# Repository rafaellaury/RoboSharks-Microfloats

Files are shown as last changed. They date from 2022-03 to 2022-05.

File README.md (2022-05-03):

# RoboSharks - MicroFloats

Welcome to the Team RoboSharks MicroFloats Github page. I hope you enjoy your stay!

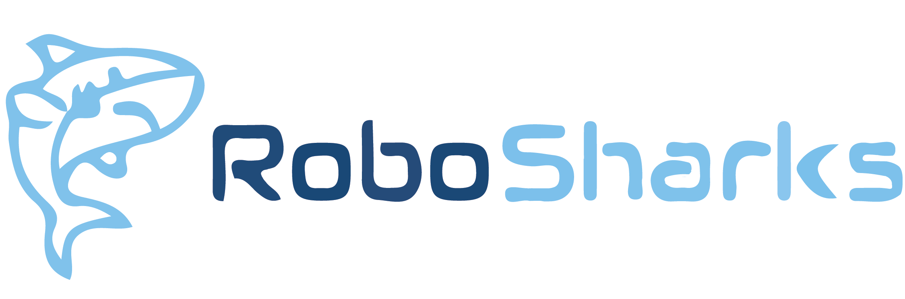
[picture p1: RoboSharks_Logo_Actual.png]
RoboSharks


MicroFloats is a project that aims to develop a swarm of autonomous underwater vehicles for ocean exploration. The current mission it is being developed for is the discovery of larval dispersion. Scientists in Stellwagen Bank, MA are researching this unknown phenomena, and the MicroFloats will greatly aid this scientific discovery effort.

MicroFloats is an ongoing project at Georgia Tech and has had several iterations of Senior Design teams and VIP teams working on it, hence the somewhat disorganized and multilayered structure. The VIP team has a helpful wiki that helps to explain some of the electronics and BMS specifics (link [here](https://github.gatech.edu/mwoodward6/LagrangianProfiler/wiki)!)

Check out our [website](https://eceseniordesign2022spring.ece.gatech.edu/sd22p17/) for more documentation and information about the project! The details of the github are explained below.

## CAD Models

This folder contains all of the CAD models in .SLDPRT format, and were created in SolidWorks. Details on measurements can be found in the fabrication package on our website.

full CAD model

## MatLab Simulations

This folder contains MatLab simulations done for the Power subsystem and antenna range. These give rough metrics for how the MicrFloat will perform since we were not able to test it in full operation.

## PCB

The PCB folder contains three subfolders, one for the Battery Management System (BMS), one for the Sensor Board, and one for the Contorl Board. These all have the most up to date KiCAD PCB schematics and board layouts in there. They also include the latest Gerber and Drill files for assembly, but it is RECOMMENDED to run a DRC again before using these pregenerated files...maybe we missed something!

## Test Code

This folder contains all the code needed to test the MicroFloat and the Sensor board in particular. 

### MicroFloat Test Code

The Arduino test Code for the whole MicroFloat came mostly from the previous team (RUR) and was adapted for our needs. Note: these files are for use with the current electronics prototyping setup, which uses an SAMD51 Thing Plus. You will have to configure your Arduino IDE to interface with this board correctly as described [here.](https://learn.sparkfun.com/tutorials/samd51-thing-plus-hookup-guide/uf2-bootloader--drivers)

The following is the documentation on each of the methods for the MicroFloats test code, taken from RUR's documentation.

The following is a brief overview and description of each test code found in the MicroFloat-Test repository. Most of the code listed is for priming the system and making sure that enough oil is in the bellows versus the reservoir to achieve neutral buoyancy. When using the following programs to calibrate oil levels, it is recommended that the electronics are off to the side so that the cap of the reservoir can be taken off, and the oil levels can be monitored. Watching the oil levels is crucial as contracting or expanding the bellows too much could cause it to pop, and expanding the bellows beyond the amount of oil in the reservoir introduces air to the system. 

*do_nothing*

This program will do as it is called, nothing. This program was written in order to test the float underwater to check neutral buoyancy. It is necessary simply because the power switch at the top of the float needs to be screwed in (and therefore the system is powered). This program ensures that the microcontroller does not send any commands. 

*full_contract*

This program will remove all oil from the bellows and into the reservoir. This would be used if trying to readjust the timings if the oil levels in the reservoir/bellows became inconsistent. This program will run once.

*full_expand*

This program will remove all the oil from the reservoir and into the bellows. This would also be used to readjust the timings if the oil levels in the reservoir/bellows became inconsistent. This program will run once.

*half_contract*

This code will remove half of the oil from the bellows, into the reservoir. This code would be run if the bellows was fully expanded with oil, and the desired state was only half expanded with oil. In this case, the float would then be at neutral buoyancy. This program will run once.

*half_expand*

This code will add half the oil from the reservoir into the bellows. This could be run if the bellows was fully contracted and the desired state was half expanded with oil. In this case, the float would then be at neutral buoyancy. This program will run once. 

*mission*

This is code to be run in a test environment. The code assumes that the starting state is with a  half contract/half expanded bellows (neutral buoyancy). It will then sink the bottom of a pool by half contracting the bellows (resulting in no oil in the bellows). It will then expand half way and wait at the bottom of the pool. The float will then expand the bellows the rest of the way to rise, and then half contract the bellows to reach neutral buoyancy again. This program runs in a loop.

### Sensor Board Test Code

The Sensor Board testing setup is described in the Final Report. Basically, it uses an ARM mbed microcontroller (hence the mbed C++ code) to send RS-232 signals to the Sensor Board, and then reads the I2C output from the Sensor Board using an Arduino. The mbed code needs to be flashed onto the mbed, and then the computer needs to be connected to the Arduino so that the serial monitor can be read to see the I2C addresses and data. The **I2C Demo** code finds the I2C addresses that are currently responding. The other programs can be used to try to get data from the Sensor Board.

## VIP Team Files

This folder contains all the VIP files at the time of our project. This could be used, but it would be better to check on the latest status on the [VIP's actual Github page](https://github.gatech.edu/Aquabots-VIP), where they have links to various useful repositories.

Have fun!

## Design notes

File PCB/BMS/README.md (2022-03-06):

# Battery Management System
For more information please check out our [wiki](https://github.gatech.edu/Aquabots-VIP/BatteryManagementSystem/wiki)!

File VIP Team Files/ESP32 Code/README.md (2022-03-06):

# This folder contains the current code to be run on the microfloat's onboard ESP32-S2

## CaptivePortal
The CaptivePortal code shows a very basic proof of concept to allow the ESP32 to broadcast its own wifi network that automatically redirects you to its webpage when upon connection. This will be necessary when testing without a convinient wifi network for the ESP to connect to but is inconvinient for development since you have to constantly switch wifi networks.

## APServer
The APServer code is where the majority of the funcioning code lives right now. It is much easier to develop code using the APServer version since it connects the ESP32 to a wifi network and allows you to access the gui like a website. Unfortunately it probably won't play nicely with gtwifi so we will need to copy the important parts back to the CaptivePortal version at some point.

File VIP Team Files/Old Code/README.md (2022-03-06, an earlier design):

# This contains the previous code from when the microfloat used a Raspberry Pi for its onboard electronics

It looks like [Lagrangian.py](https://github.gatech.edu/mwoodward6/LagrangianProfiler/blob/master/Old%20Code/Lagrangian.py) is the code designed to run on the Raspberry Pi. There is also [LagrangianSerialLine.py](https://github.gatech.edu/mwoodward6/LagrangianProfiler/blob/master/Old%20Code/LagrangianSerialLine.py) which seems to have been used for manually testing the profiler out of the water (I would recommend focusing more on Lagrangian.py).

[TestControlGui.py](https://github.gatech.edu/mwoodward6/LagrangianProfiler/blob/master/Old%20Code/TestControlGUI.py) seems to be the newest version of the GUI.

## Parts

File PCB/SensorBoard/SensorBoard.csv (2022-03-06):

Id | Designator | Package | Quantity | Designation | Supplier and ref
1 | C8,C7,C6,C5,C4,C3 | C_0603_1608Metric_Pad1.05x0.95mm_HandSolder | 6 | 0.1uF
2 | J1 | PinHeader_2x03_P2.54mm_Vertical | 1 | Power Header
3 | J2 | PinHeader_2x03_P2.54mm_Vertical | 1 | Signal Header
4 | REF**,REF**,REF** | MountingHole_3.2mm_M3_Pad_Via | 3 | MountingHole_3.2mm_M3_Pad_Via
5 | U6,U5,U4,U3 | TSSOP-16_4.4x5mm_P0.65mm | 4 | SC16IS740IPWQ900
6 | U2 | VSSOP-10_3x3mm_P0.5mm | 1 | ADS1115IDGST
7 | U1 | SSOP-28_5.3x10.2mm_P0.65mm | 1 | MCP23017_SS
8 | RLY4,RLY3,RLY2,RLY1,RLY0 | SOP-4_3.8x4.1mm_P2.54mm | 5 | CPC1002NTR
9 | R12,R11,R10,R9,R8,R3,R2,R1,R0 | R_0805_2012Metric_Pad1.15x1.40mm_HandSolder | 9 | 1k
10 | R4 | R_0805_2012Metric_Pad1.15x1.40mm_HandSolder | 1 | 10k
11 | J4 | Molex_Nano-Fit_105314-xx10_2x05_P2.50mm_Horizontal | 1 | Sensor 0
12 | J5 | Molex_Nano-Fit_105314-xx10_2x05_P2.50mm_Horizontal | 1 | Sensor 1
13 | J6 | Molex_Nano-Fit_105314-xx10_2x05_P2.50mm_Horizontal | 1 | Sensor 2
14 | J7 | Molex_Nano-Fit_105314-xx10_2x05_P2.50mm_Horizontal | 1 | Sensor 3
15 | CRYS1 | Crystal_HC49-U_Vertical | 1 | LFXTAL003033BULK
16 | C2 | C_0603_1608Metric_Pad1.05x0.95mm_HandSolder | 1 | 33pf
17 | C1 | C_0603_1608Metric_Pad1.05x0.95mm_HandSolder | 1 | 22pf

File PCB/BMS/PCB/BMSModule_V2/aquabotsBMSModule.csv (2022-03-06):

Id | Designator | Package | Quantity | Designation | Supplier and ref
1 | ATTINY841 | SOIC-14_3.9x8.7mm_P1.27mm | 1 | ATtiny841-SSU
2 | C2 | C_0805_2012Metric | 1 | 1uF
3 | C5,C4 | C_0805_2012Metric | 2 | 22pF
4 | D2 | D_SMB | 1 | SMBJ5.0A
5 | F1 | Fuse_1812_4532Metric | 1 | mSMD150
6 | POWER1 | JST_PH_S2B-PH-K_1x02_P2.00mm_Horizontal | 1 | Battery
7 | Q1 | SOT-23 | 1 | AO3400A
8 | R3 | R_0805_2012Metric | 1 | 6.8K
9 | R4 | R_0805_2012Metric | 1 | 2.7K
10 | R5 | R_0805_2012Metric | 1 | 220OHMS
11 | R8,R12,R25,R26,R29,R30,R24,R6,R22,R32,R39,R33,R31,R36,R38,R35,R34,R37 | R_2010_5025Metric | 18 | 3.3OHM 3/4W
12 | R16 | R_0805_2012Metric | 1 | 4.7KOHMS
13 | R18 | R_0805_2012Metric | 1 | 2.2KOHMS
14 | R19 | R_0805_2012Metric | 1 | CMFB103F3950FANT
15 | R20,R1,R15 | R_0805_2012Metric | 3 | 10KOHMS
16 | RX1 | JST_PH_S2B-PH-K_1x02_P2.00mm_Horizontal | 1 | RX Connector
17 | TX1 | JST_PH_S2B-PH-K_1x02_P2.00mm_Horizontal | 1 | TX Connector
18 | Y1 | Crystal_SMD_5032-2Pin_5.0x3.2mm | 1 | 8MHZ Ceramic Resonator
19 | D4 | LED_0805_2012Metric | 1 | Blue
20 | C1 | C_0805_2012Metric | 1 | 100nF
21 | U1 | SOP-4_4.4x2.6mm_P1.27mm | 1 | EL3H7(B)(TA)-G
22 | R2 | R_0805_2012Metric | 1 | 1KOHMS
23 | D1 | SOT-23 | 1 | AZ432ANTR-E1
24 | R14 | R_0805_2012Metric | 1 | 510OHMS

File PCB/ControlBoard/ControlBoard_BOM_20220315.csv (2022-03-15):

Id | Designator | Package | Quantity | Designation | Supplier and ref
1 | U5 | SOP65P640X110-21N | 1 | TPS75233QPWPR
2 | J8 | USB_C_Receptacle_HRO_TYPE-C-31-M-12 | 1 | USB_C_Receptacle_USB2.0
3 | J3,J4,J5,J6 | Molex_Nano-Fit_105314-xx08_2x04_P2.50mm_Horizontal | 4 | Conn_02x04_Odd_Even
4 | U7 | ublox_NEO | 1 | NEO-M9N
5 | U3 | ESP32-S2-WROOM | 1 | ESP32-S2-WROOM
6 | R29,R36 | R_0603_1608Metric | 2 | 470R
7 | U14,U15 | SOP-4_4.4x2.6mm_P1.27mm | 2 | FODM217C
8 | R31,R38 | R_0603_1608Metric | 2 | 100R
9 | R30,R21,R37 | R_0603_1608Metric | 3 | 100k
10 | Q1,Q3 | SOT-23 | 2 | DMP3030SN-7
11 | D1,D2 | D_0603_1608Metric | 2 | D_Schottky
12 | J2 | PinHeader_2x03_P2.54mm_Vertical | 1 | Power Header
13 | J7 | PinHeader_2x03_P2.54mm_Vertical | 1 | Signal Header
14 | BT1 | BR-1632A_HAN | 1 | BATT_BCKP
15 | C1,C11,C12,C18,C24,C27,C31 | C_0603_1608Metric | 7 | 10uF
16 | C2,C6,C8,C9,C10,C13,C16,C19,C21,C23,C26,C42,C44 | C_0603_1608Metric | 13 | 0.1uF
17 | C3 | C_0603_1608Metric | 1 | 15 uF
18 | C4,C5,C14,C15 | C_0603_1608Metric | 4 | 20pF
19 | C7 | C_0603_1608Metric | 1 | 22uF
20 | C17,C33,C36,C37,C38 | C_1206_3216Metric | 5 | 22uF
21 | C22,C29 | C_0603_1608Metric | 2 | 1.0uF
22 | C34,C35,C39 | C_0603_1608Metric | 3 | 100nF
23 | C40 | C_0805_2012Metric | 1 | 200nF
24 | C41,C43 | CAPC6153X670N | 2 | 22uF
25 | F1,F4 | Fuse_0603_1608Metric | 2 | 2A
26 | F2,F3 | Fuse_0603_1608Metric | 2 | 3A
27 | FB1,FB2 | L_0603_1608Metric | 2 | 1.5A
28 | J1 | U.FL_Hirose_U.FL-R-SMT-1_Vertical | 1 | Conn_Coaxial
29 | J9 | microSD_HC_Wuerth_693072010801 | 1 | Micro_SD_Card
30 | L1 | L_0805_2012Metric | 1 | 2.2 uH
31 | L3 | Vishay-IHLP-3232DZ-FP_2.413x5.334-3D_4.0-0-0-MFG | 1 | 3.3uH
32 | L4 | L_Wuerth_WE-LQS-8040 | 1 | 12uH
33 | Q2 | SOT-23 | 1 | SST3906HZGT116
34 | R1,R8 | R_0603_1608Metric | 2 | 1M
35 | R2 | R_0603_1608Metric | 1 | 732k
36 | R3,R6,R12,R13,R15,R16,R18,R19,R20,R23,R26,R27,R28 | R_0603_1608Metric | 13 | 10k
37 | R4,R5 | R_0603_1608Metric | 2 | 22
38 | R9 | R_0603_1608Metric | 1 | 365k
39 | R14 | R_0603_1608Metric | 1 | 200k
40 | R17 | R_0603_1608Metric | 1 | 54.9k
41 | R22 | R_0603_1608Metric | 1 | 5.23k
42 | R24,R25 | R_0603_1608Metric | 2 | 5.1k
43 | R32,R34 | R_0603_1608Metric | 2 | 1k
44 | R33 | R_0603_1608Metric | 1 | 27k
45 | SW1 | SW_Push_SPST_NO_Alps_SKRK | 1 | Reset
46 | SW2 | SW_Push_SPST_NO_Alps_SKRK | 1 | Boot
47 | SW3 | SW_DIP_SPSTx04_Slide_6.7x11.72mm_W8.61mm_P2.54mm_LowProfile | 1 | SW_DIP_x04
48 | U1 | TSOT-23-5 | 1 | LM3670MF
49 | U2,U6 | MSOP-12-1EP_3x4mm_P0.65mm_EP1.65x2.85mm_ThermalVias | 2 | LTC4419
50 | U4 | InvenSense_QFN-24_3x3mm_P0.4mm | 1 | ICM-20948
51 | U8 | Bosch_LGA-8_2.5x2.5mm_P0.65mm_ClockwisePinNumbering | 1 | BME280
52 | U9 | LR62E | 1 | LR62E
53 | U10 | TSSOP-8_3x3mm_P0.65mm | 1 | PCA9306DP
54 | U11 | SOT-23-6 | 1 | TPS565201
55 | U12 | SOT-23-6 | 1 | TPS54202DDR
56 | U13 | SOT-23-6 | 1 | USBLC6-2SC6
57 | Y1 | Crystal_SMD_3215-2Pin_3.2x1.5mm | 1 | 32.768KHz 12.5p
58 | C25 | C_1206_3216Metric | 1 | 47uF

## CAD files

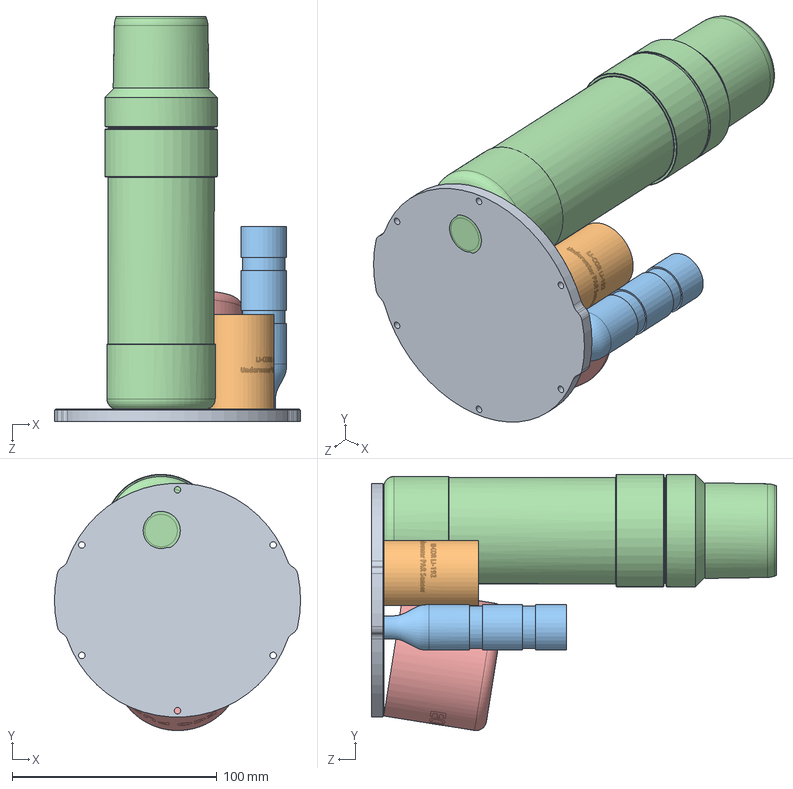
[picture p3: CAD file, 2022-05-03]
CAD Models/Sensors and Top Cap Assembly/Sensor-Top Cap Assembly.SLDASM
120.3 x 125.2 x 198.0 mm
Blue Robotics End Cap
PAR Sensor
Mini CTD
8262-000-28 - Nano SST final assembly with pressure PA-4LD cable connection_Substitute_2.stp
ECO PUCK

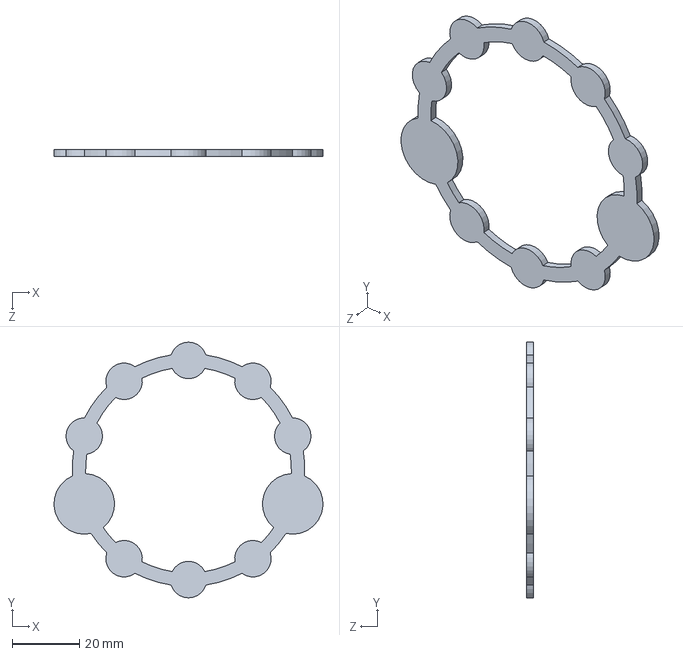
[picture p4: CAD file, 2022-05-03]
CAD Models/BMS_Assembly/Bottom_Bus_Full.SLDPRT
79.8 x 75.9 x 2.03 mm

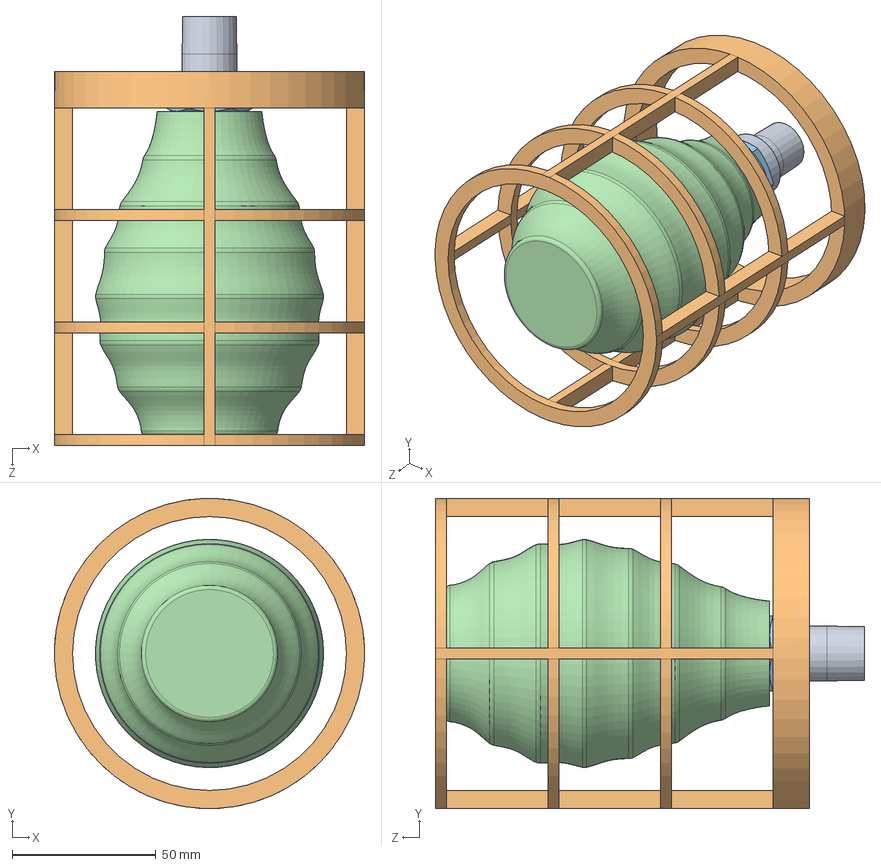
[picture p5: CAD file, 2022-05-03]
CAD Models/Bottom Cap Assembly/RoboSharks Bottom Cap Assembly.SLDASM
108.0 x 108.0 x 149.2 mm
RUR - Pressed Fitting Adaptor
Bellows Cage
4810T364_British Standard Low-Pressure Stainless Steel Pipe Fitting
Bellows

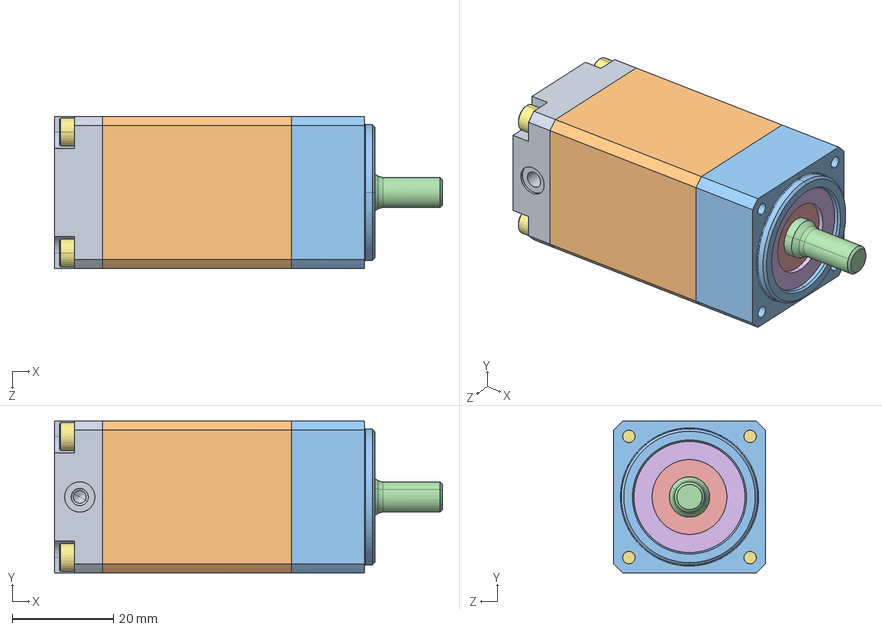
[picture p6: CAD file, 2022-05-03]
CAD Models/Internal Assembly/Takako - Pump - TFH-040.SLDASM
76.8 x 30.0 x 30.0 mm
Part9.IGS
Part10.IGS
Part13.IGS
Part13.1.IGS
Part13.1.2.IGS
Part16.IGS
Part20.IGS x 4

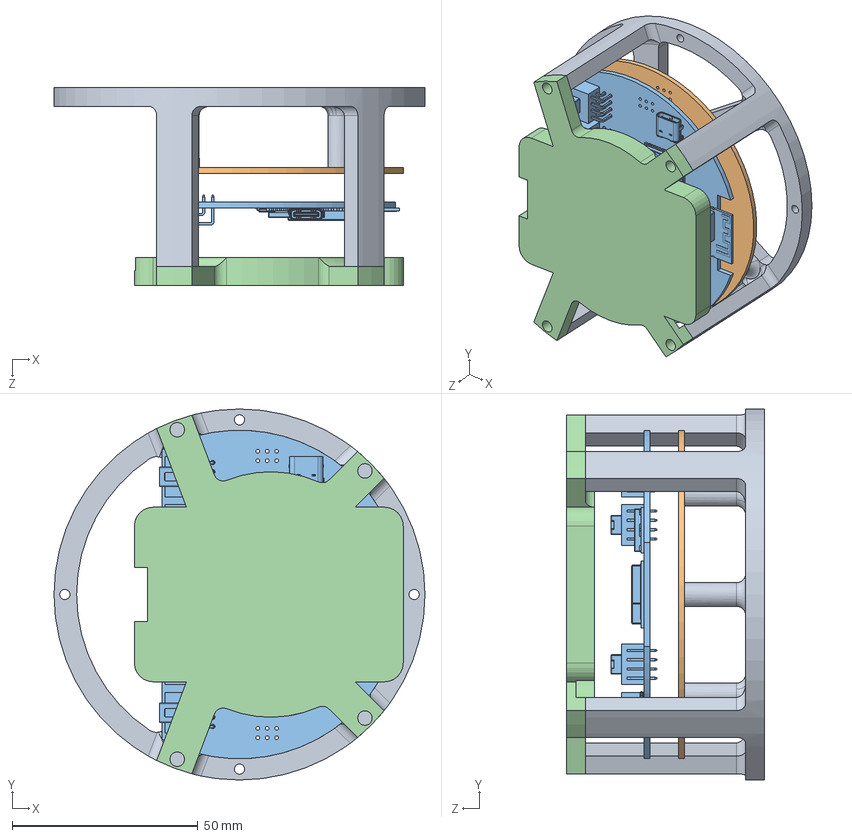
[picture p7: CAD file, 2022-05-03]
CAD Models/PCB files/Electronics Mount Assembly Final.SLDASM
99.8 x 99.8 x 53.3 mm
RoboSharks Electronics Mount
SensorBoard
ControlBoard
Mount Attachment
aquabotsBMSController

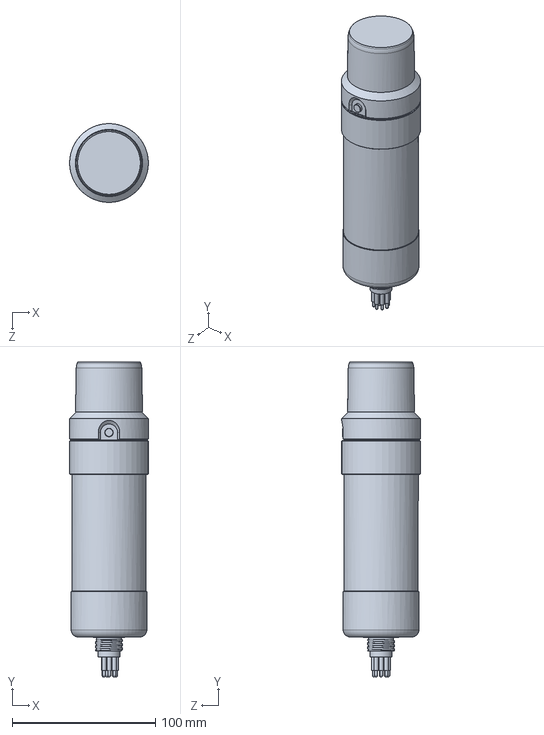
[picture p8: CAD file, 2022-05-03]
CAD Models/Sensors and Top Cap Assembly/Nano with Connector.SLDASM
55.0 x 219.9 x 55.0 mm

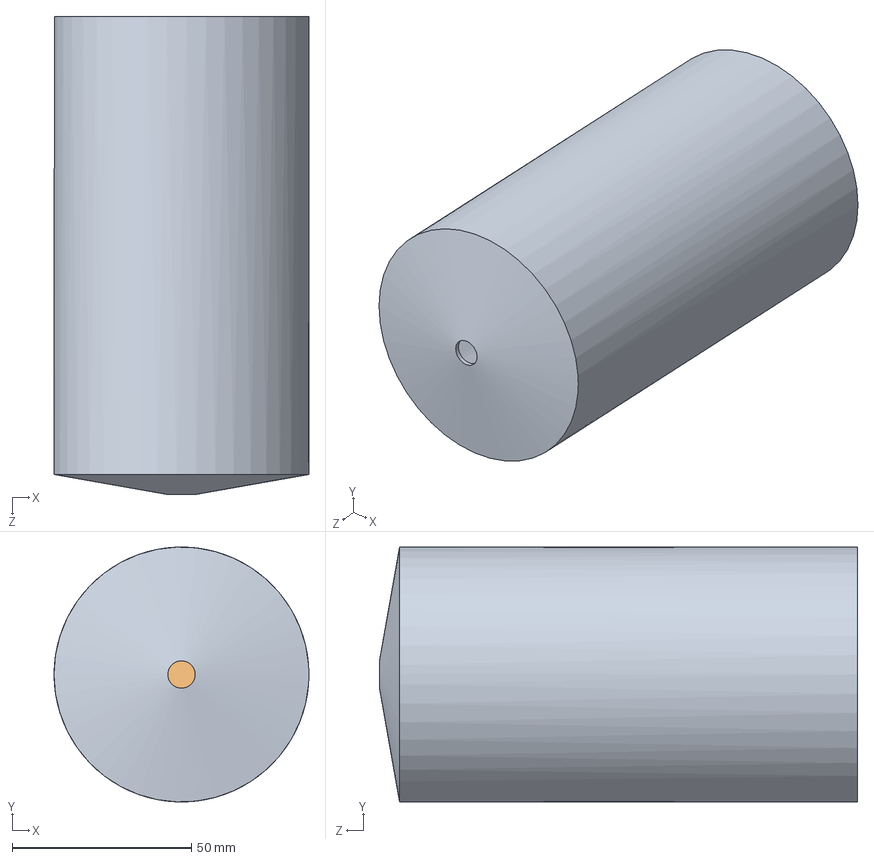
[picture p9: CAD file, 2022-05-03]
CAD Models/Syringe Assembly.SLDASM
71.1 x 71.1 x 133.4 mm
Syringe
Syringe Plunger

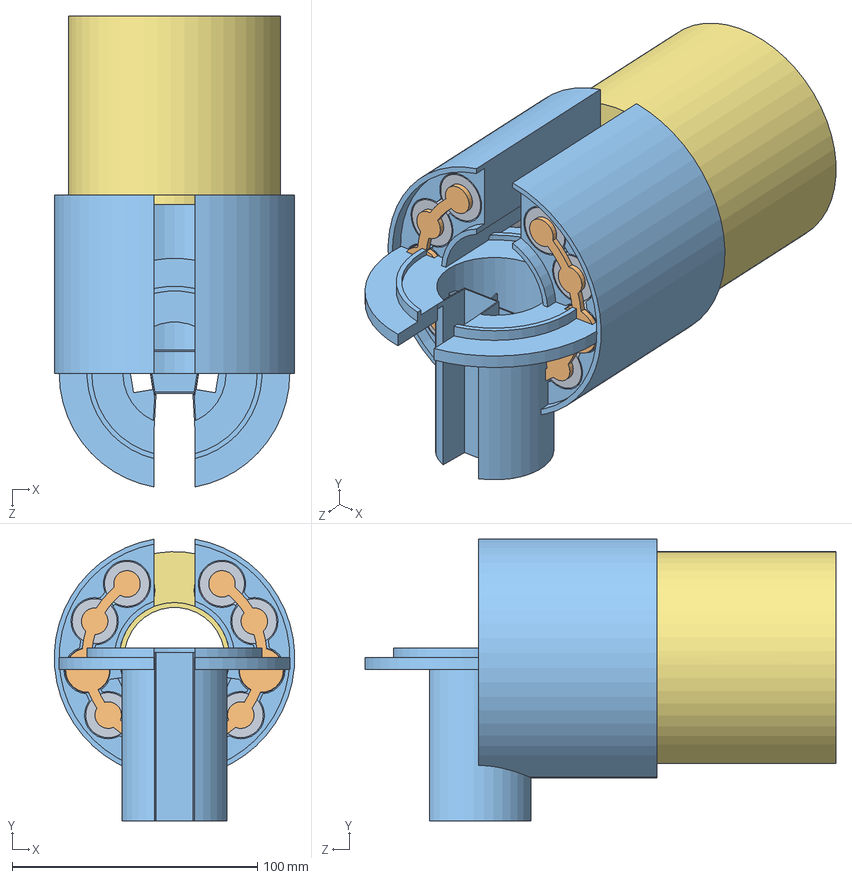
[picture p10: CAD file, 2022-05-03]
CAD Models/BMS_Assembly/BMS_Assembly.SLDASM
97.9 x 114.8 x 191.9 mm
Top_Array
Top_Bus_Half x 2
Top_Case
Bottom_Cap
Bottom_Bus_Full
Bottom_Array
Bottom Case
Bottom_Bus_Half_1
Bottom_Bus_Half_2
Top_Bus_Full
Top_Cap

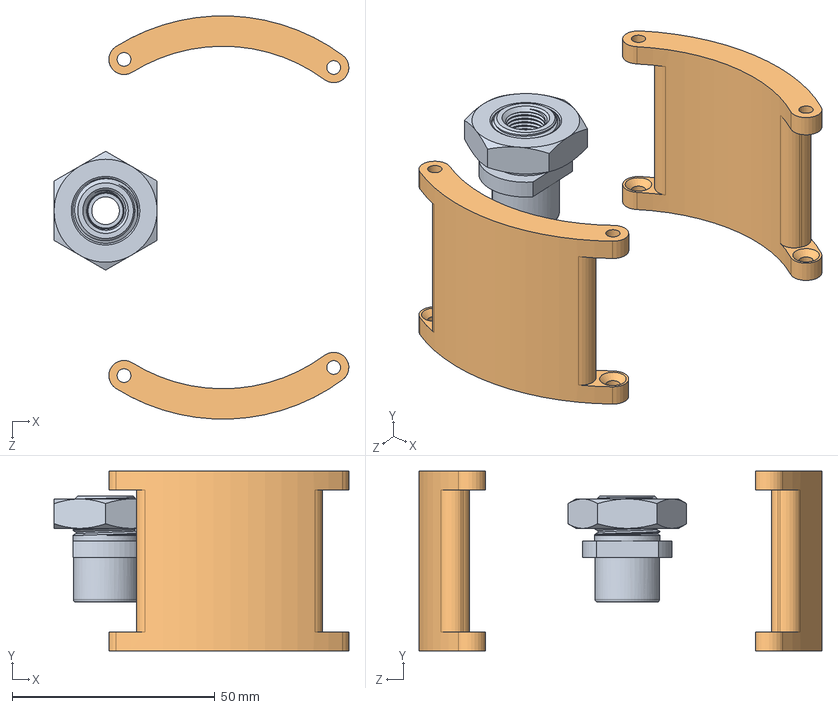
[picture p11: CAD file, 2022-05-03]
CAD Models/Internal Assembly/RUR - Reservoir Assembly.SLDASM
72.7 x 44.3 x 99.4 mm
McMaster - Through Wall Fitting - 8674T54
RUR - Standoff Reservoir x 2

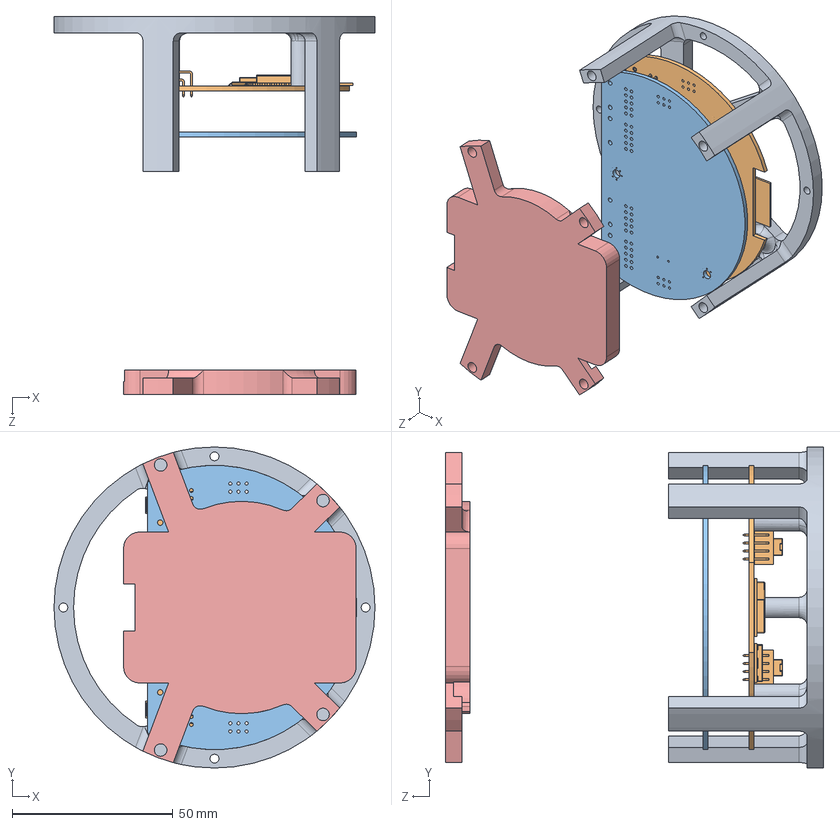
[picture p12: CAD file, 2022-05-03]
CAD Models/PCB files/PCBs and Mount Assembly.SLDASM
99.8 x 99.8 x 117.6 mm
RoboSharks Electronics Mount
ControlBoard
SensorBoard
aquabotsBMSController
Mount Attachment

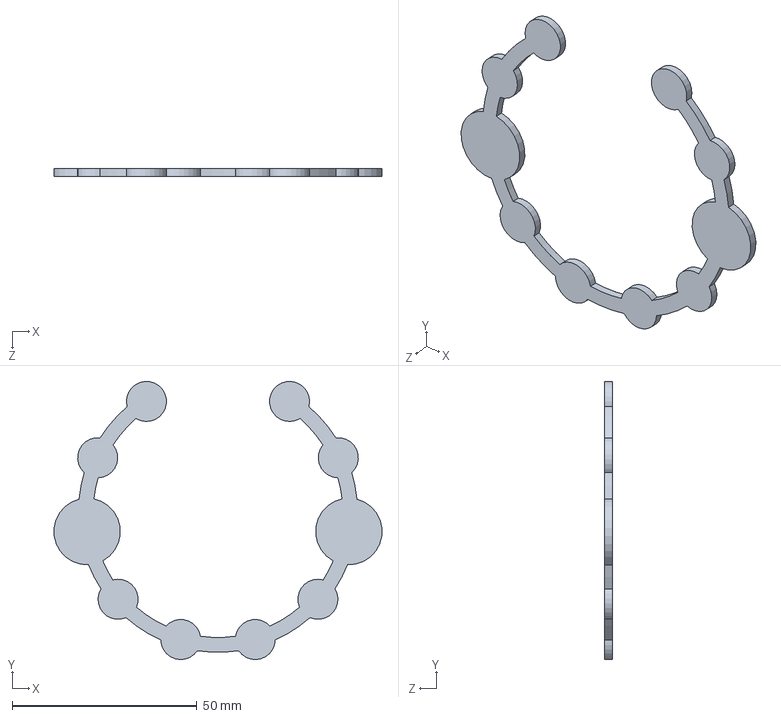
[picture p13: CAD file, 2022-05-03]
CAD Models/BMS_Assembly/Top_Bus_Full.SLDPRT
88.7 x 75.2 x 2.03 mm

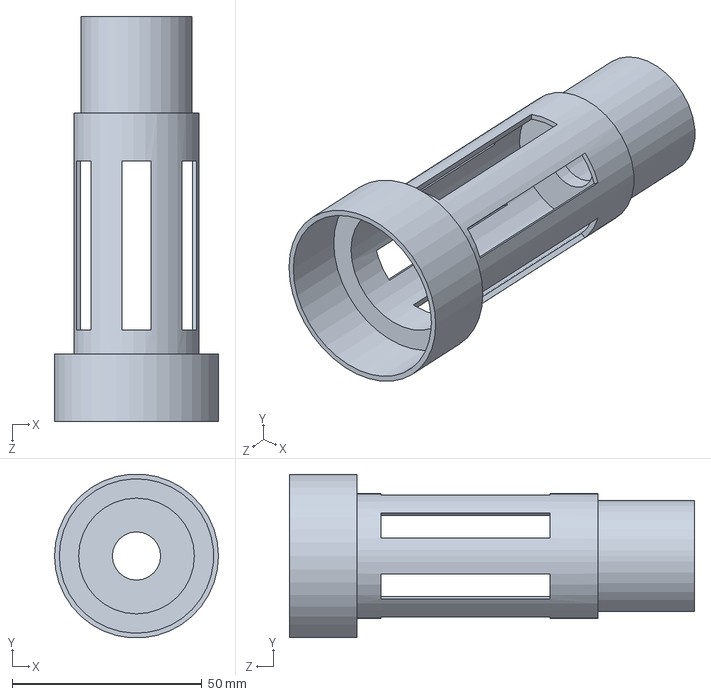
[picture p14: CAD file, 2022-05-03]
CAD Models/Antenna/Antenna Mount.SLDPRT
43.2 x 43.0 x 106.7 mm

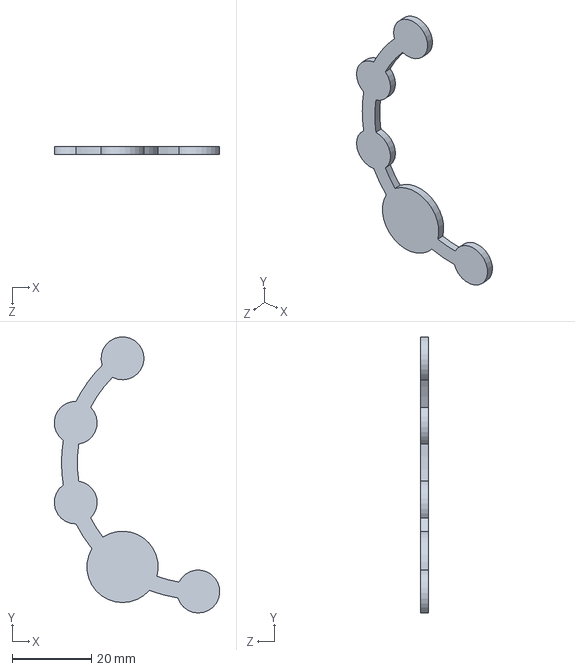
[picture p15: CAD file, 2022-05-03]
CAD Models/BMS_Assembly/Bottom_Bus_Half_2.SLDPRT
41.8 x 69.7 x 2.03 mm

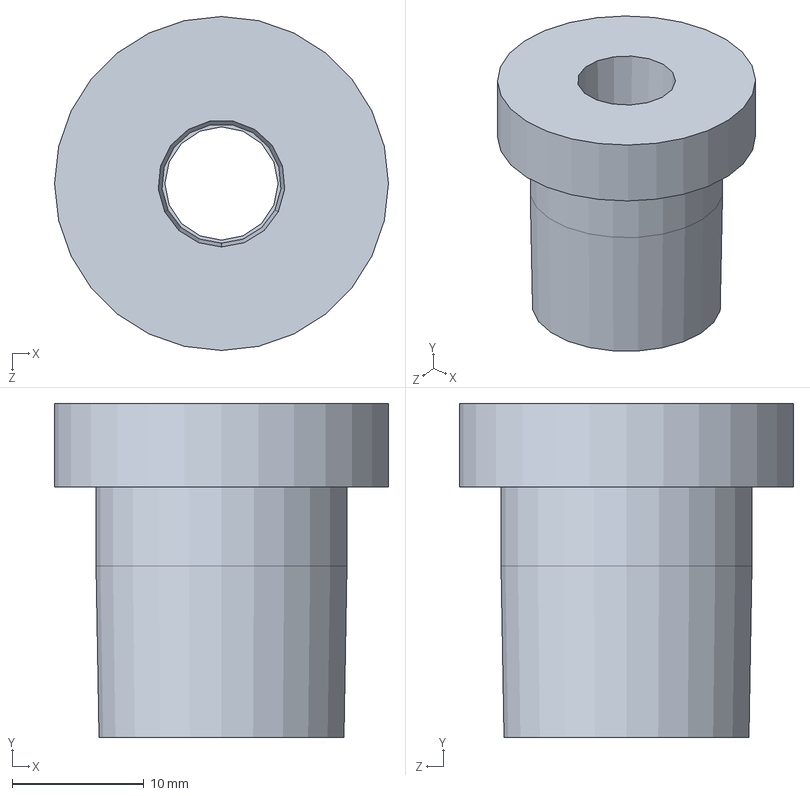
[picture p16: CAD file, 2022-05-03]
CAD Models/Bottom Cap Assembly/RUR - Pressed Fitting Adaptor.SLDPRT
25.4 x 25.4 x 25.4 mm

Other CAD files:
CAD Models/Internal Assembly/DevBoard.SLDPRT
CAD Models/PCB files/Mount Attachment.SLDPRT
CAD Models/RUR - Mid Flange.SLDPRT
CAD Models/Sensors and Top Cap Assembly/TO PRINT/ECO PUCK.STL
CAD Models/BMS_Assembly/BMS_Module.SLDPRT
CAD Models/BMS_Assembly/Battery.SLDPRT
CAD Models/BMS_Assembly/Bottom Case.SLDPRT
CAD Models/BMS_Assembly/Bottom_Array.SLDPRT
CAD Models/BMS_Assembly/Bottom_Bus_Half_1.SLDPRT
CAD Models/BMS_Assembly/Bottom_Cap.SLDPRT
CAD Models/BMS_Assembly/Module_Enclosure.SLDPRT
CAD Models/BMS_Assembly/Top_Array.SLDPRT
CAD Models/BMS_Assembly/Top_Bus_Half.SLDPRT
CAD Models/BMS_Assembly/Top_Cap.SLDPRT
CAD Models/BMS_Assembly/Top_Case.SLDPRT
CAD Models/Battery Drawings/Battery.SLDDRW
CAD Models/Battery Drawings/Bottom Bus Full.SLDDRW
CAD Models/Battery Drawings/Bottom Bus Half 1.SLDDRW
CAD Models/Battery Drawings/Bottom Bus Half 2.SLDDRW
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

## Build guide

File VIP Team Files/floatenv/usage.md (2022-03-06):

# Setting Up #
1. Creating a new virtual environment for this project is recommended.
2. `pip install gym` to install the Gym package, which is required.
3. Change directory to the floatenv folder that has `setup.py`, and `pip install -e .` to install the float environment as a package.

## Training Deep RL Models (Optional) with Stable Baselines ##
1. `pip install tensorflow==1.14.0` to install the TensorFlow package, which is required for the next package to be installed. Note that newer versions of TensorFlow are not compatible.
2. `pip install stable-baselines` to install the package containing the implementations of the RL algorithms.

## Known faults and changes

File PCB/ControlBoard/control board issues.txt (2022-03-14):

Design Issues:
LR62E no data lines connected
NEO-M8N/NEO-M9N D_SEL is tied to ground which disables I2C mode
Should change connection for the SD card from native to serial or talk to Dr. West and figure out what storage solution he actually wants
Should have added debug points for the ESP32 (at least pins 37 and 38 for flashing over uart)
Ideally we would like to add 2 extra external connectors to signal the ESP32 to turn everything on, probably just connect J5 pin 5 to power and 6 to a GPIO with pulldown resistor so you can pull it high by shorting the pins
Might need to come up with a method of charging the Backup Battery, even if its just adding an extra set of throughholes to clip some leads on or something

Layout Issues:
Need cutout for the USB-C port so you can actually plug a cable in
Would be nice to move U14 and U15 further up so its safer to clamp the board in a vise

Part Selection Issues:
I think the purchased headers are 1mm instead of 2.54mm, need to find the correct version
Level shifter for 1.8V was out of stock, I think its back now though
12v reg out of stock so didn't solder most of those components
LTC4419s for power source selection out of stock, soldered wire for USB5V and non-backup 3V3

Soldering Issues
Mishap with leak detect, soldered resistor onto pad
5V->3V3 regulator tore a ground pad, seems totally fine
USB protection (USBLC6) out of stock so soldered wire across the two lines
Redundant Fuse 3 replaced with wire
1.8V reg out of stock, not soldered
Termperature Humidity Pressure Sensor (BME280) is soldered but untested, might be kind of sketchy
LR62E is a little crooked, don't think it is a problem but worth keeping an eye on
Reused NEO-M8N from RUR team, it looks like they may have gotten it a little too warm, not sure if it works or not
USB D- pad damaged while fixing a different issue, ran a mod wire
D1 and D2 are super sketchy looking, might want to test those if you're going to use them

Current Power Issues:
5V Regulator needs to be tested with load applied

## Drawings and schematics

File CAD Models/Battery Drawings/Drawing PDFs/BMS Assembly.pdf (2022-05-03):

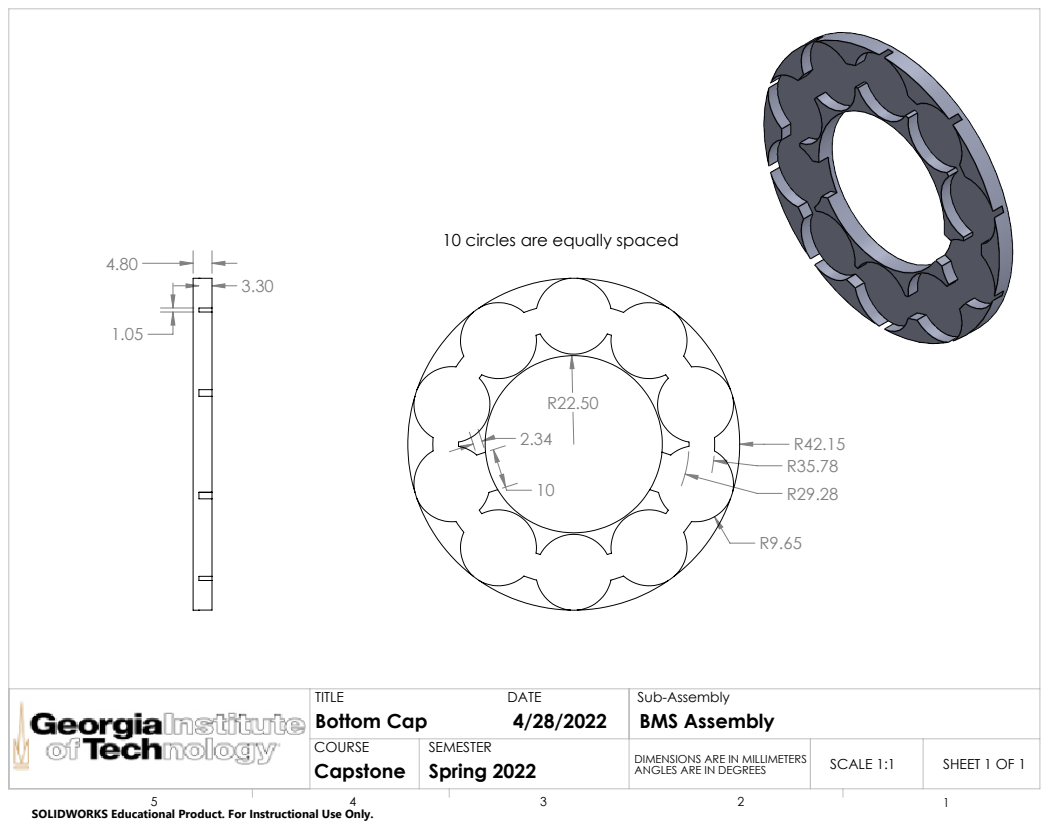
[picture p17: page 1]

10 circles are equally spaced

TITLE DATE Bottom Cap 4/28/2022 | Sub-Assembly BMS Assembly

COURSE Capstone | SEMESTER Spring 2022 | ANGLES ARE IN DEGREES | SCALE 1:1 | SHEET 1 OF 1 DIMENSIONS ARE IN MILLIMETERS

SOLIDWORKS Educational Product. For Instructional Use Only.

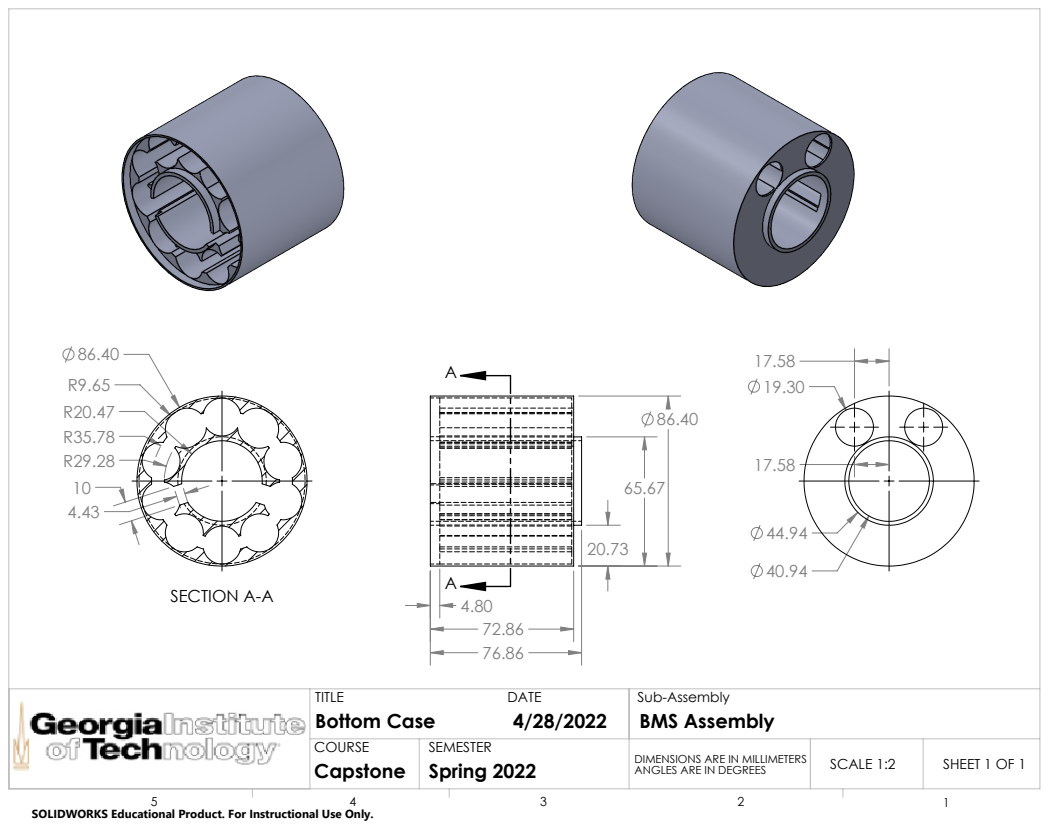
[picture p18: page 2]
SECTION A-A

TITLE DATE Bottom Case 4/28/2022 | Sub-Assembly BMS Assembly

COURSE | SEMESTER | | SCALE 1:2 | SHEET 1 OF 1 DIMENSIONS ARE IN MILLIMETERS

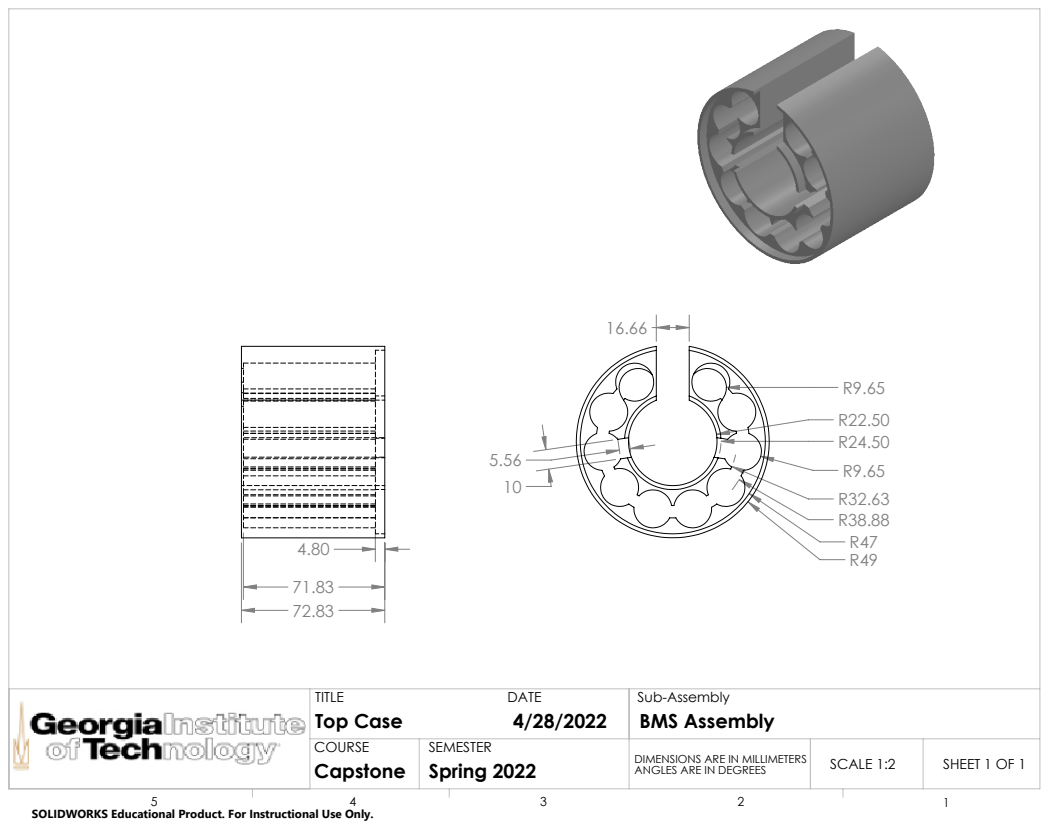
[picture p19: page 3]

TITLE DATE Top Case 4/28/2022 | Sub-Assembly BMS Assembly

COURSE | SEMESTER | | SCALE 1:2 | SHEET 1 OF 1 DIMENSIONS ARE IN MILLIMETERS

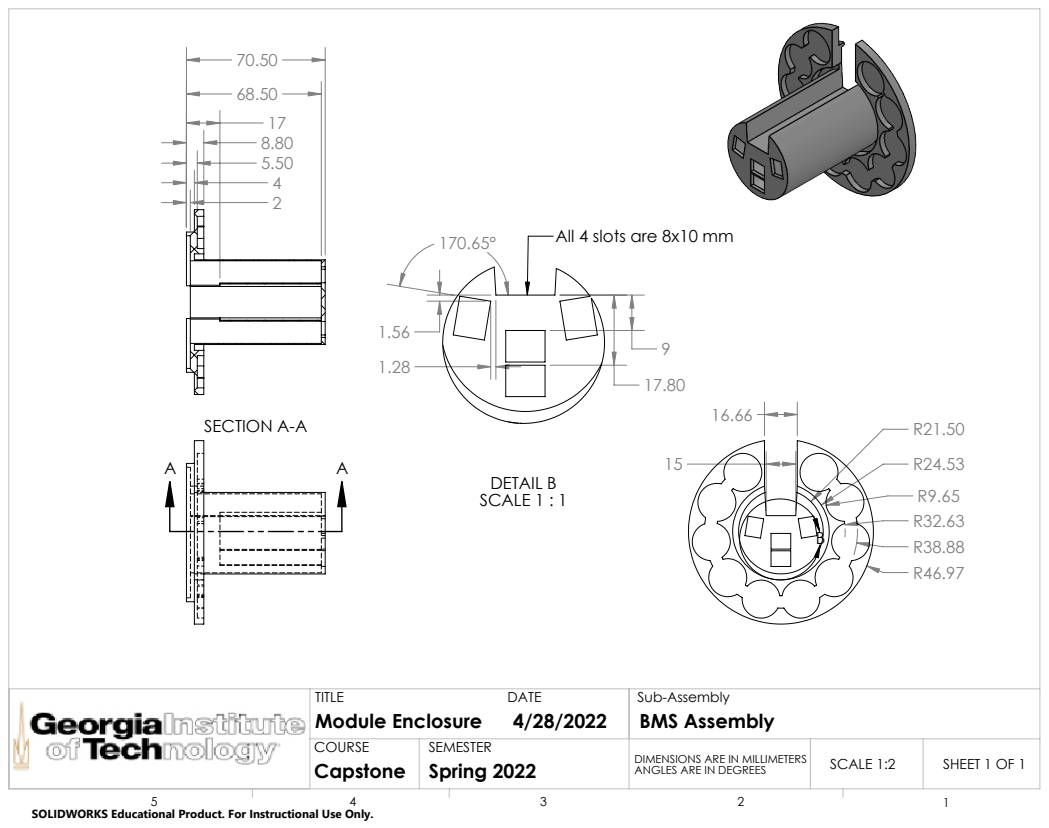
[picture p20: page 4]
SECTION A-A; DETAIL B SCALE 1 : 1

All 4 slots are 8x10 mm

TITLE DATE Module Enclosure 4/28/2022 | Sub-Assembly BMS Assembly

COURSE | SEMESTER | | SCALE 1:2 | SHEET 1 OF 1 DIMENSIONS ARE IN MILLIMETERS

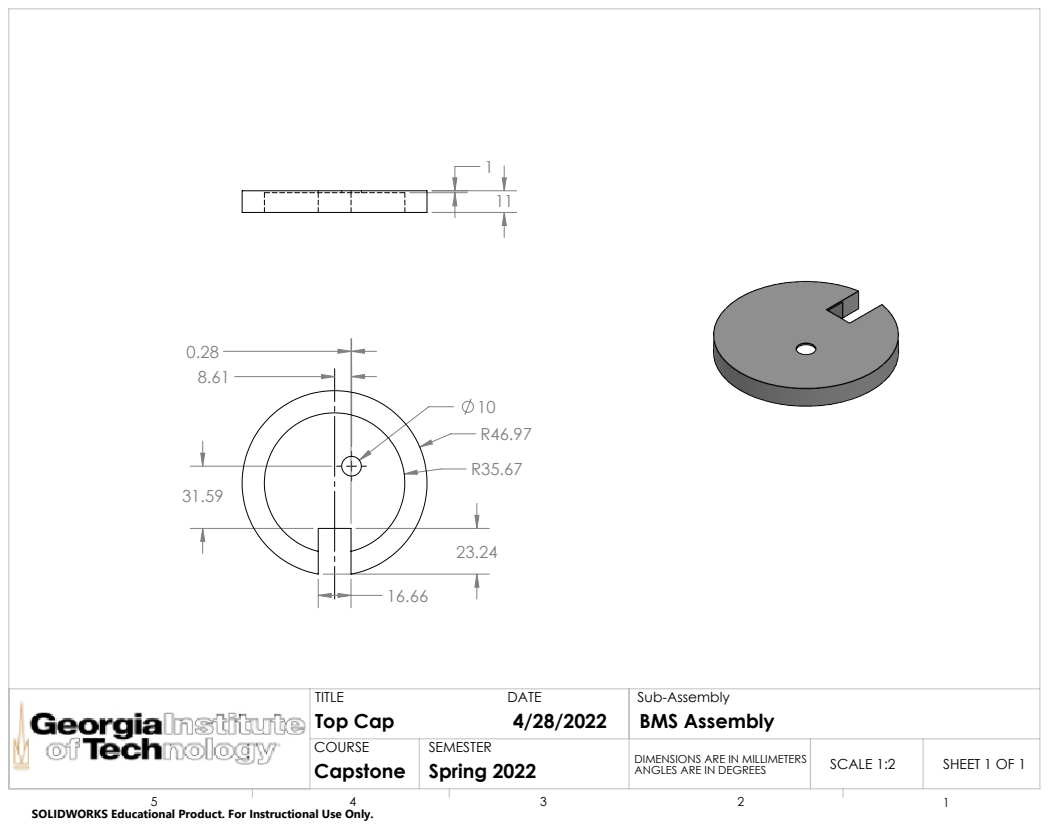
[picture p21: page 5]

TITLE DATE Top Cap 4/28/2022 | Sub-Assembly BMS Assembly

COURSE | SEMESTER | | SCALE 1:2 | SHEET 1 OF 1 DIMENSIONS ARE IN MILLIMETERS

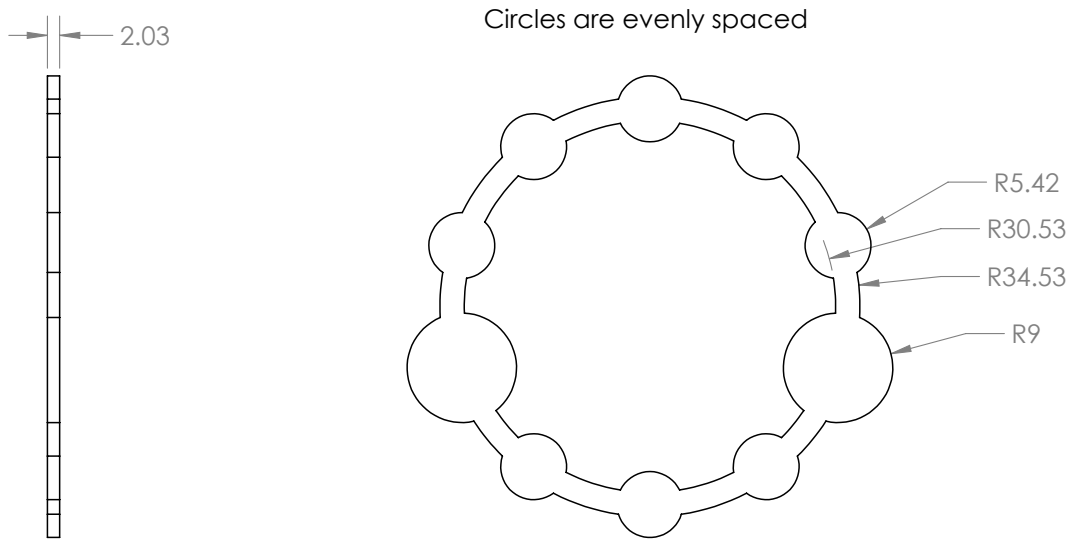
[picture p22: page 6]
Circles are evenly spaced

TITLE DATE Bottom Bus Full 4/28/2022 | Sub-Assembly BMS Assembly

COURSE | SEMESTER | | SCALE 1:1 | SHEET 1 OF 1 DIMENSIONS ARE IN MILLIMETERS

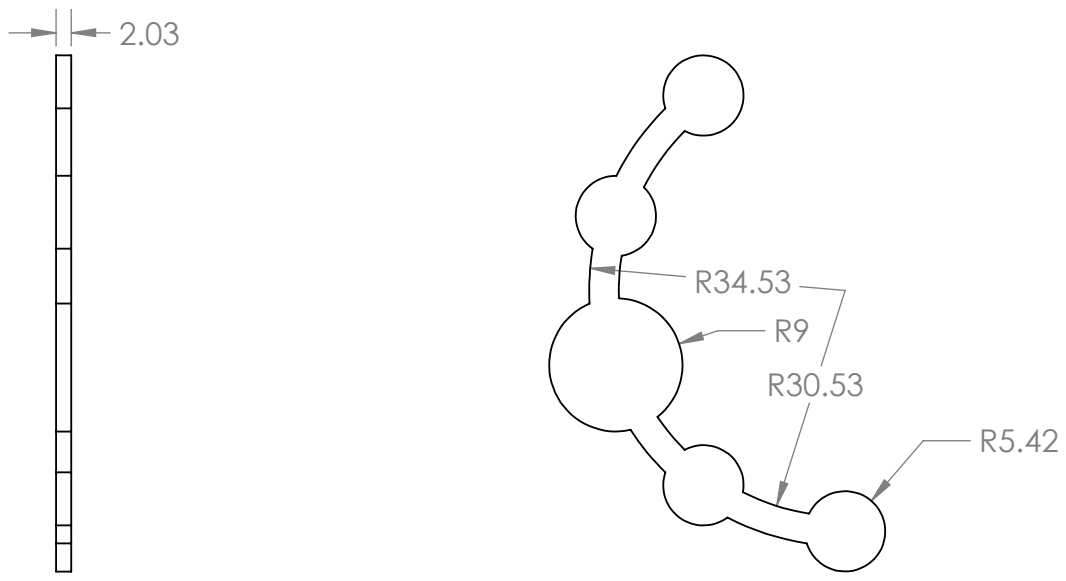
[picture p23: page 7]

TITLE DATE Bottom Bus Half 1 4/28/2022 | Sub-Assembly BMS Assembly

COURSE | SEMESTER | | SCALE 1:1 | SHEET 1 OF 1 DIMENSIONS ARE IN MILLIMETERS

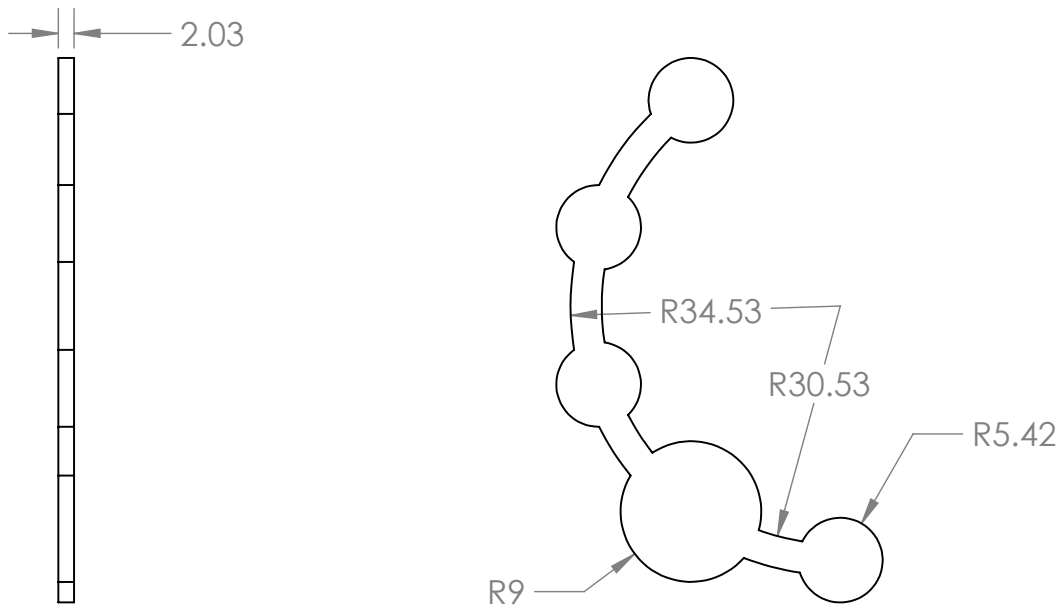
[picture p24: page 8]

TITLE DATE Bottom Bus Half 2 4/28/2022 | Sub-Assembly BMS Assembly

COURSE | SEMESTER | | SCALE 1:1 | SHEET 1 OF 1 DIMENSIONS ARE IN MILLIMETERS

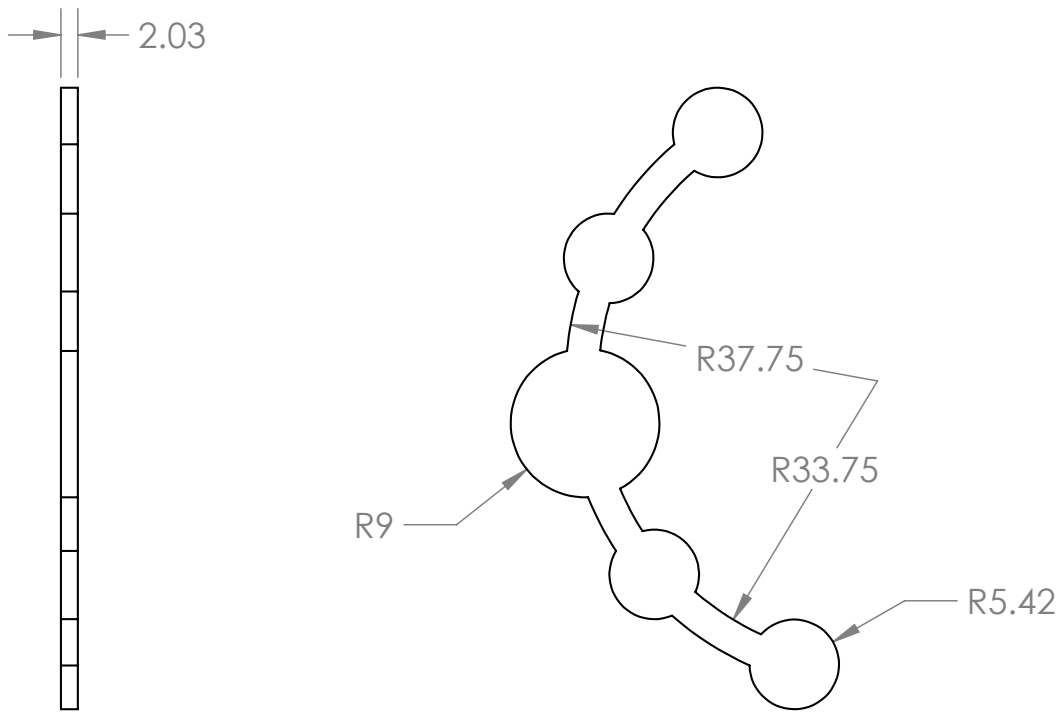
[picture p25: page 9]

TITLE DATE Top Bus Half 4/28/2022 | Sub-Assembly BMS Assembly

COURSE | SEMESTER | | SCALE 1:1 | SHEET 1 OF 1 DIMENSIONS ARE IN MILLIMETERS

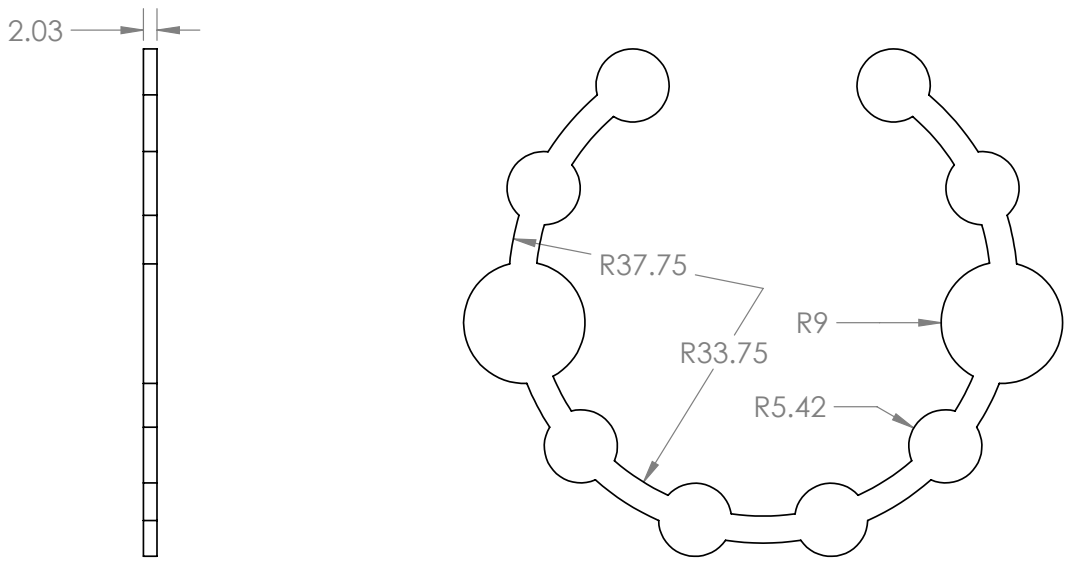
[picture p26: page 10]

TITLE DATE Top Bus Full 4/28/2022 | Sub-Assembly BMS Assembly

COURSE | SEMESTER | | SCALE 1:1 | SHEET 1 OF 1 DIMENSIONS ARE IN MILLIMETERS

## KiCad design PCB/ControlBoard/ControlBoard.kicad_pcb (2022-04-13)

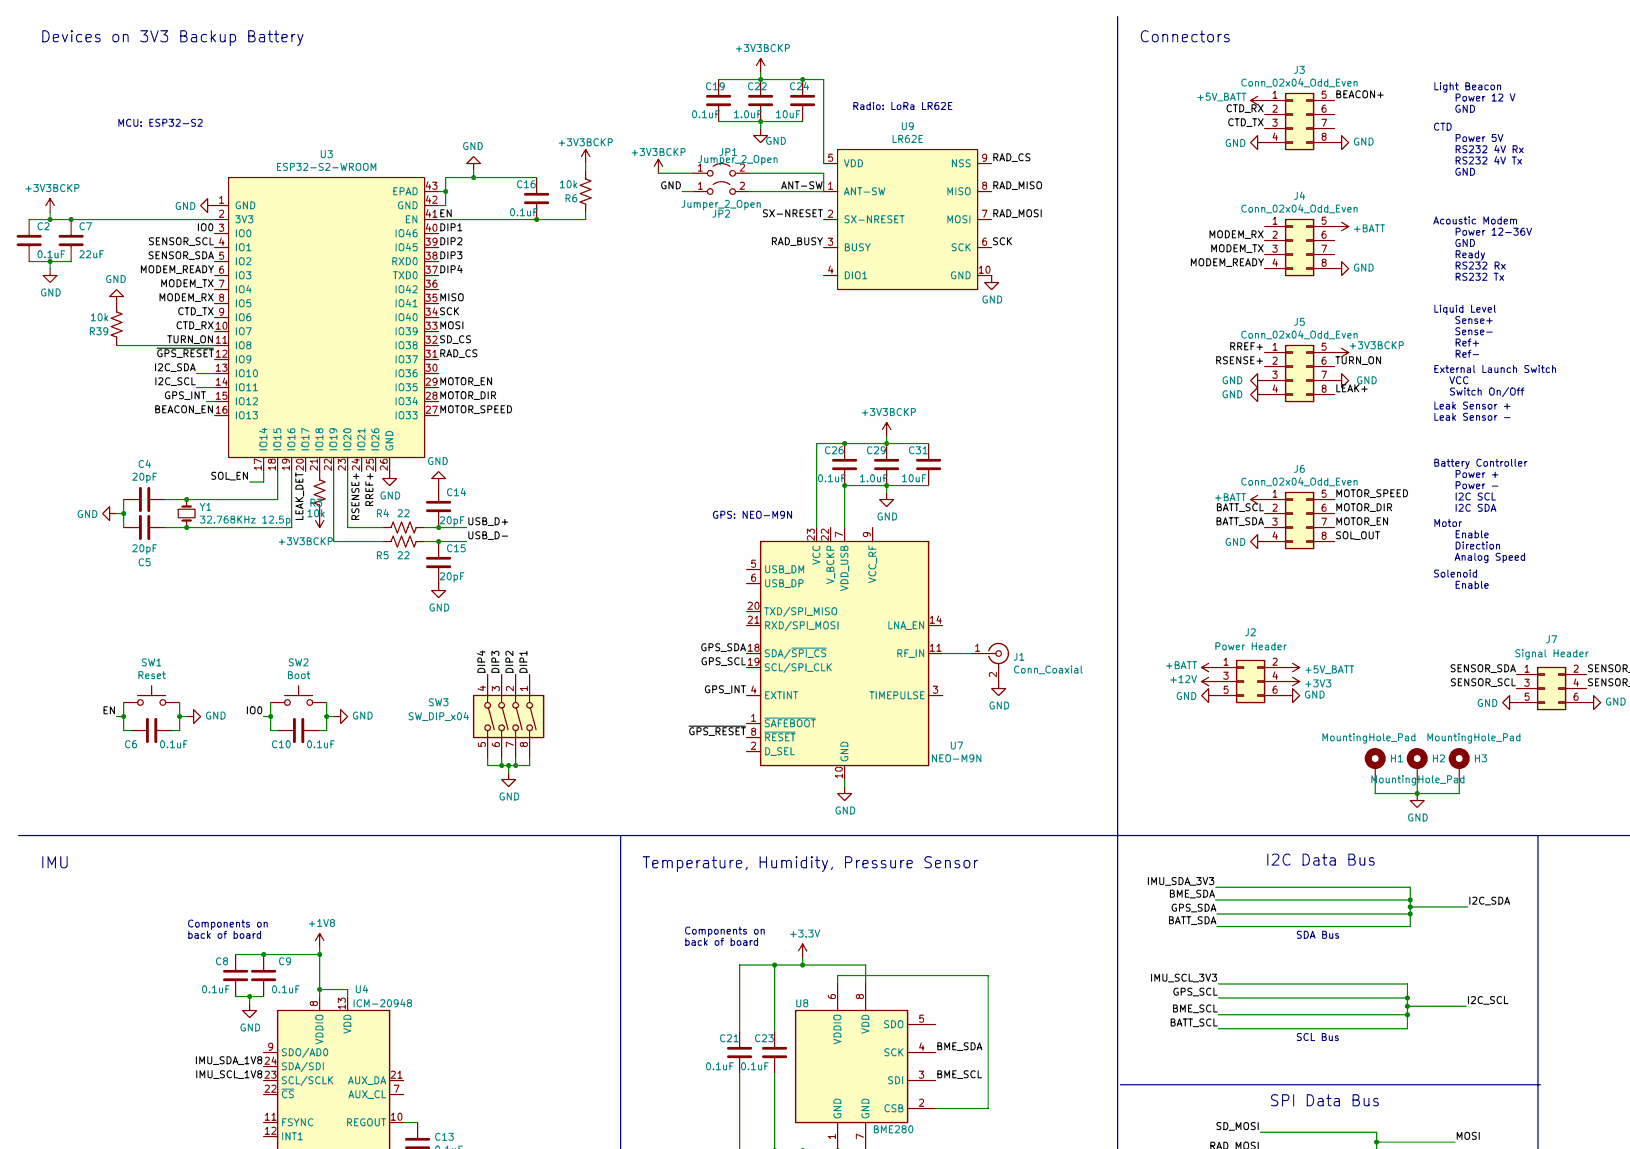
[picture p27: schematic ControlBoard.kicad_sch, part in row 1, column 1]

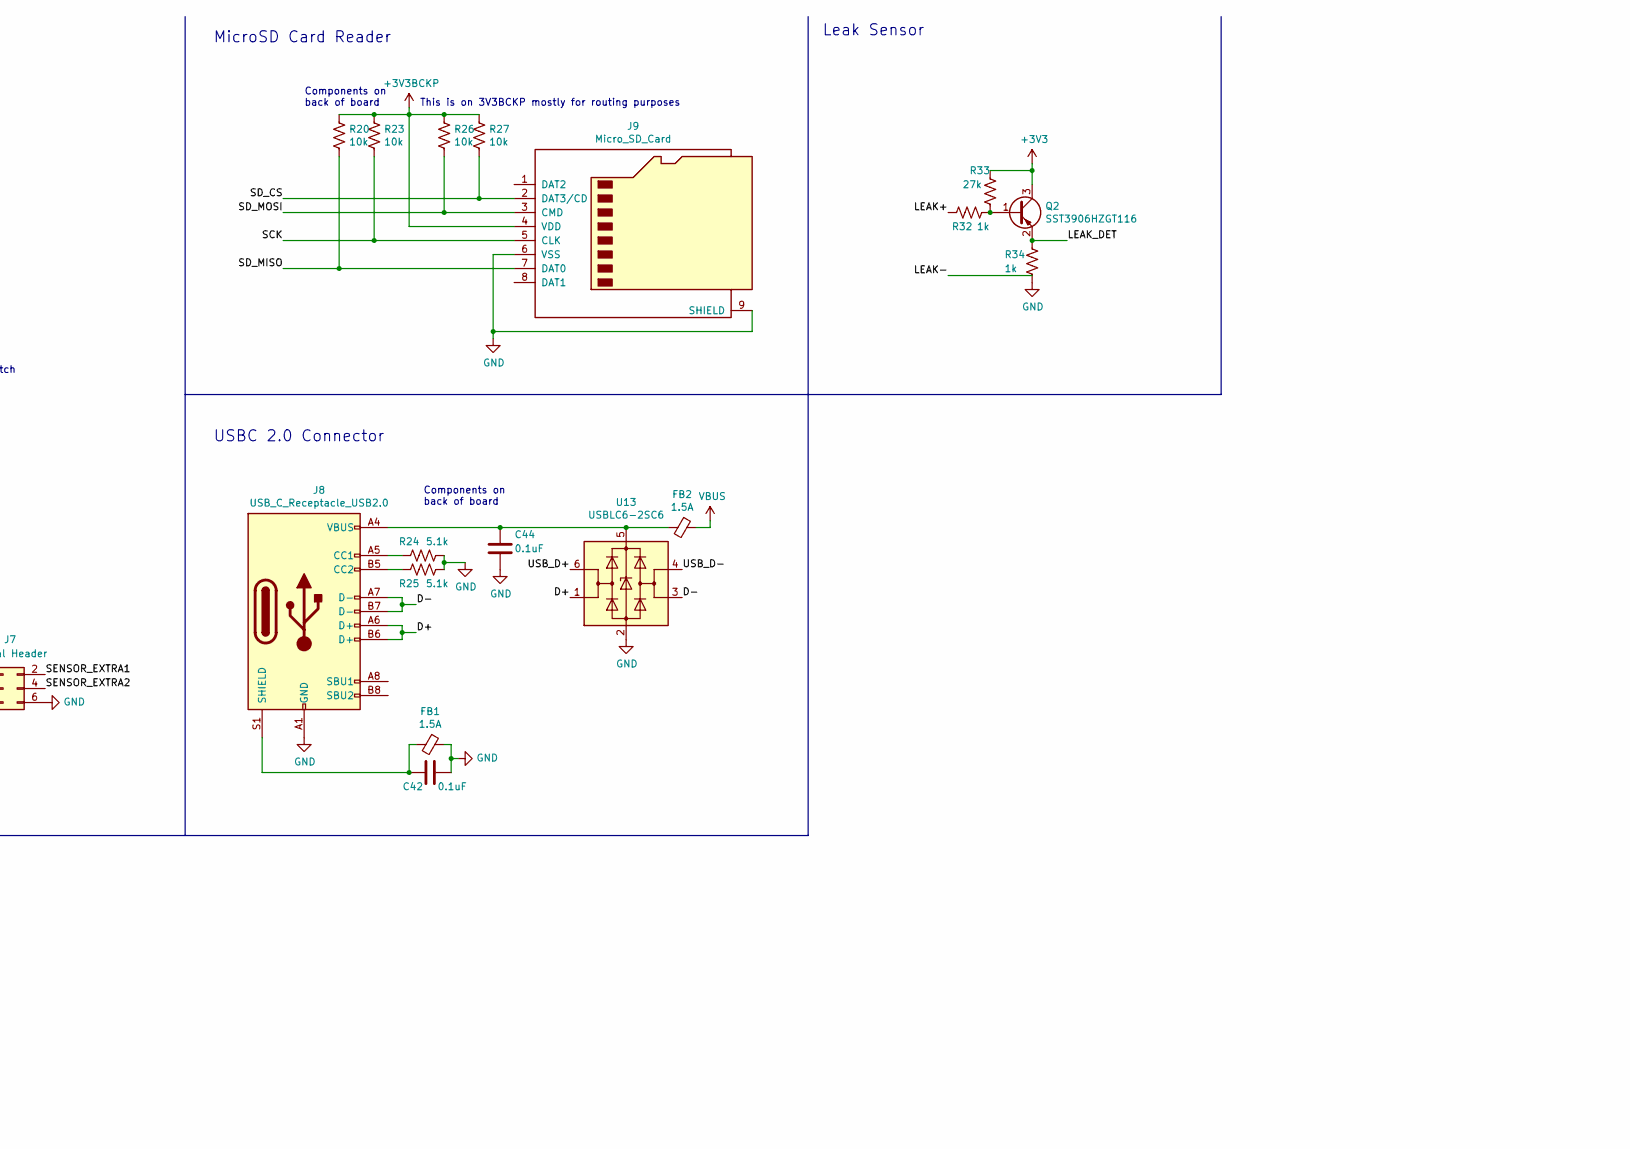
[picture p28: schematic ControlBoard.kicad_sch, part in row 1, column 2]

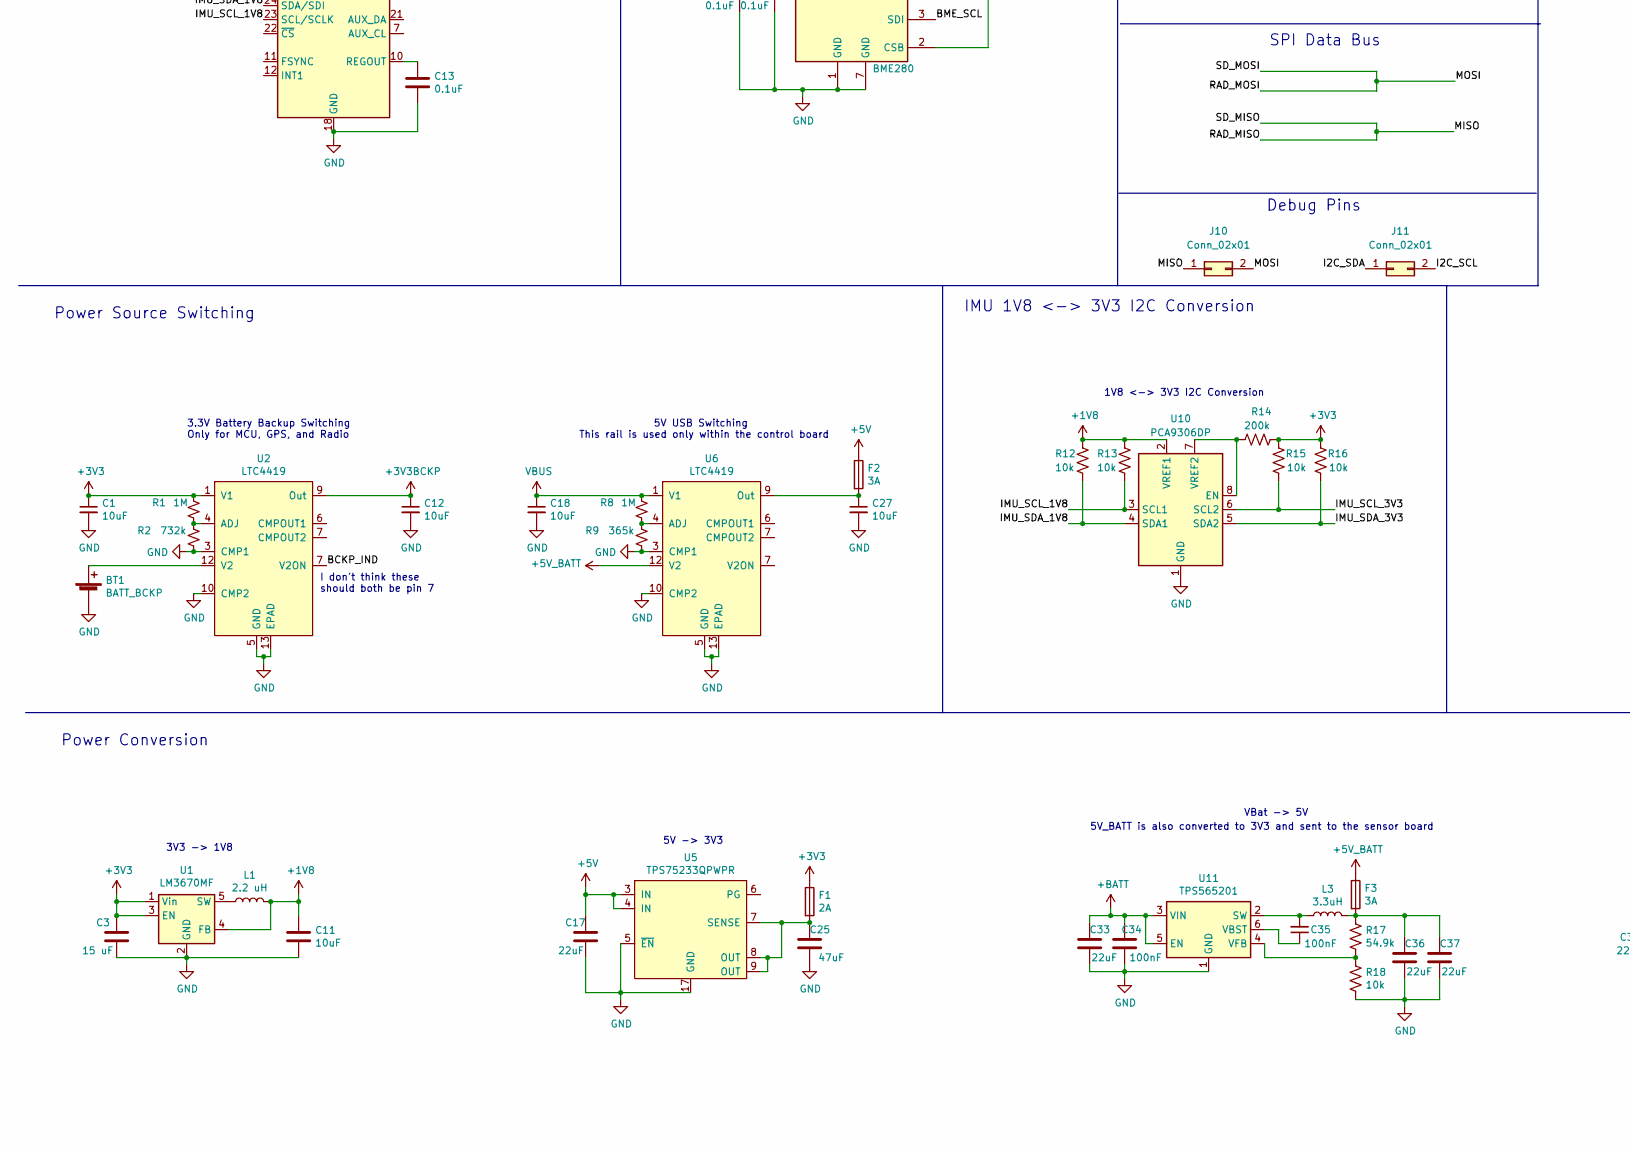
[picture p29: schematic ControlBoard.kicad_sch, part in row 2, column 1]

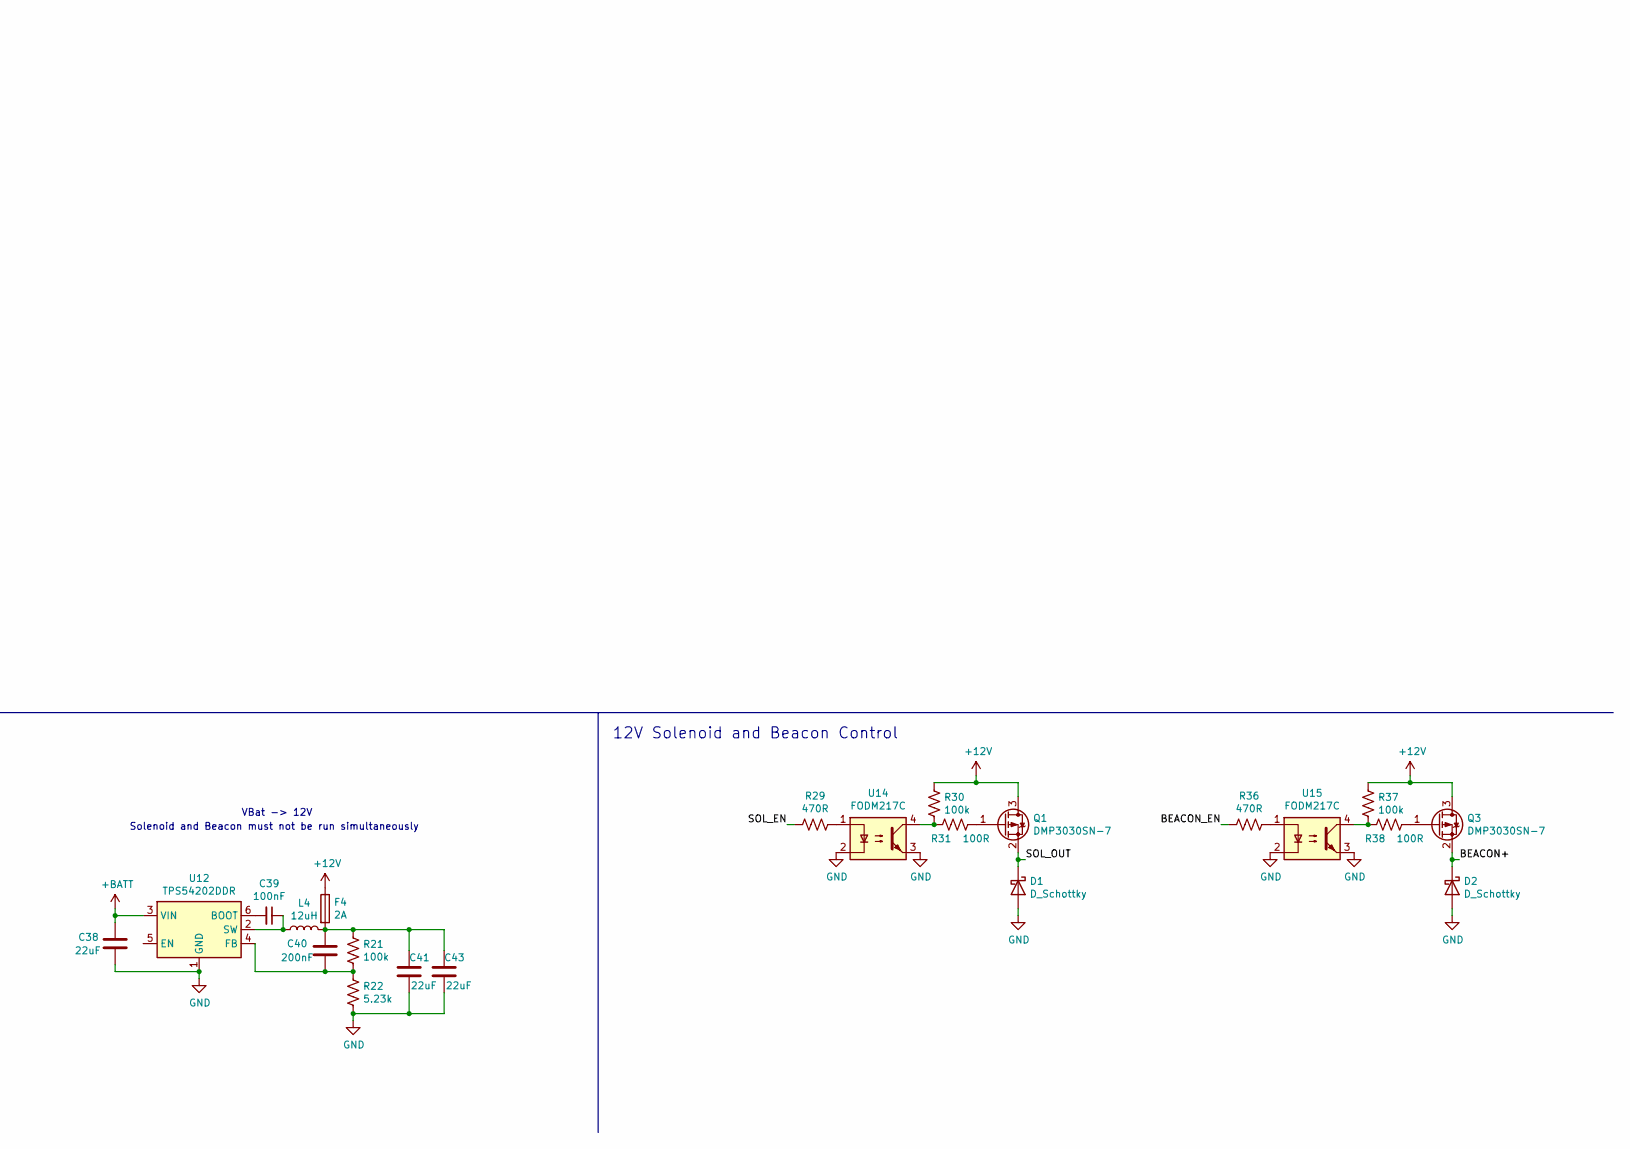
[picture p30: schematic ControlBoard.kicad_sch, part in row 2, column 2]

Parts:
BT1: BATT_BCKP; BatteryHolder_Keystone_3000_1x12mm
C1, C11, C12, C18, C24, C27, C31: 10uF; C_0603_1608Metric
C2, C6, C8, C9, C10, C13, C16, C19, C21, C23, C26, C42, C44: 0.1uF; C_0603_1608Metric
C3: 15 uF; C_0603_1608Metric
C4, C5, C14, C15: 20pF; C_0603_1608Metric
C7: 22uF; C_0603_1608Metric
C17, C33, C36, C37, C38: 22uF; C_1206_3216Metric
C22, C29: 1.0uF; C_0603_1608Metric
C25: 47uF; C_1206_3216Metric
C34, C35, C39: 100nF; C_0603_1608Metric
C40: 200nF; C_0805_2012Metric
C41, C43: 22uF; CAPC6153X670N
D1, D2: D_Schottky; D_0603_1608Metric
F1, F4: 2A; Fuse_0603_1608Metric
F2, F3: 3A; Fuse_0603_1608Metric
FB1, FB2: 1.5A; L_0603_1608Metric
H1, H2, H3: MountingHole_Pad; MountingHole_3.2mm_M3_Pad_Via
J1: Conn_Coaxial; U.FL_Hirose_U.FL-R-SMT-1_Vertical
J2: Power Header; PinHeader_2x03_P2.54mm_Vertical
J3, J4, J5, J6: Conn_02x04_Odd_Even; Molex_Nano-Fit_105314-xx08_2x04_P2.50mm_Horizontal
J7: Signal Header; PinHeader_2x03_P2.54mm_Vertical
J8: USB_C_Receptacle_USB2.0; USB_C_Receptacle_HRO_TYPE-C-31-M-12
J9: Micro_SD_Card; microSD_HC_Wuerth_693072010801
J10, J11: Conn_02x01; PinHeader_2x01_P2.54mm_Vertical
JP1, JP2: Jumper_2_Open; SolderJumper-2_P1.3mm_Open_Pad1.0x1.5mm
L1: 2.2 uH; L_0805_2012Metric
L3: 3.3uH; Vishay-IHLP-3232DZ-FP_2.413x5.334-3D_4.0-0-0-MFG
L4: 12uH; L_Wuerth_WE-LQS-8040
Q1, Q3: DMP3030SN-7; SOT-23
Q2: SST3906HZGT116; SOT-23
R1, R8: 1M; R_0603_1608Metric
R2: 732k; R_0603_1608Metric
R3, R6, R12, R13, R15, R16, R18, R20, R23, R26, R27, R39: 10k; R_0603_1608Metric
R4, R5: 22; R_0603_1608Metric
R9: 365k; R_0603_1608Metric
R14: 200k; R_0603_1608Metric
R17: 54.9k; R_0603_1608Metric
R21, R30, R37: 100k; R_0603_1608Metric
R22: 5.23k; R_0603_1608Metric
R24, R25: 5.1k; R_0603_1608Metric
R29, R36: 470R; R_0603_1608Metric
R31, R38: 100R; R_0603_1608Metric
R32, R34: 1k; R_0603_1608Metric
R33: 27k; R_0603_1608Metric
SW1: Reset; SW_Push_SPST_NO_Alps_SKRK
SW2: Boot; SW_Push_SPST_NO_Alps_SKRK
SW3: SW_DIP_x04; SW_DIP_SPSTx04_Slide_6.7x11.72mm_W8.61mm_P2.54mm_LowProfile
U1: LM3670MF; TSOT-23-5
U2, U6: LTC4419; MSOP-12-1EP_3x4mm_P0.65mm_EP1.65x2.85mm_ThermalVias
U3: ESP32-S2-WROOM
U4: ICM-20948; InvenSense_QFN-24_3x3mm_P0.4mm
U5: TPS75233QPWPR; SOP65P640X110-21N
U7: NEO-M9N; ublox_NEO
U8: BME280; Bosch_LGA-8_2.5x2.5mm_P0.65mm_ClockwisePinNumbering
U9: LR62E
U10: PCA9306DP; TSSOP-8_3x3mm_P0.65mm
U11: TPS565201; SOT-23-6
U12: TPS54202DDR; SOT-23-6
U13: USBLC6-2SC6; SOT-23-6
U14, U15: FODM217C; SOP-4_4.4x2.6mm_P1.27mm
Y1: 32.768KHz 12.5p; Crystal_SMD_3215-2Pin_3.2x1.5mm

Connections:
+1V8: C8.1, C9.1, C11.1, L1.2, R12.2, R13.2, U1.4 (FB), U4.8 (VDDIO), U4.13 (VDD), U10.2 (VREF1)
+3.3BCKP: C2.1, C7.1, C12.1, C19.1, C22.1, C24.1, C26.1, C29.1, C31.1, J5.5, J9.4 (VDD), JP1.1 (A), R3.2, R6.2, R20.1, R23.1, R26.1, R27.1, U2.9 (Out), U3.2 (3V3), U7.23 (VCC), U9.5 (VDD)
+5V: C17.1, F2.1, U5.3 (IN), U5.4 (IN)
+5_BATT: F3.1, J2.2, J3.1, U6.12 (V2)
+12V: F4.1, J2.3, Q1.3 (D), Q3.3 (D), R30.1, R37.1
+BATT: C33.2, C34.2, C38.2, J2.1, J4.5, J6.1, U11.3 (VIN), U11.5 (EN), U12.3 (VIN)
/ANT-SW: JP1.2 (B), JP2.2 (B), U9.1 (ANT-SW)
/BATT_SCL: J6.2, J11.2, R15.2, U3.14 (IO11), U7.19 (SCL/SPI_CLK), U8.3 (SDI), U10.6 (SCL2)
/BATT_SDA: J6.3, J11.1, R16.2, U3.13 (IO10), U7.18 (SDA/~SPI_CS), U8.4 (SCK), U10.5 (SDA2)
/BCKP_IND: U2.7 (V2ON)
/BEACON+: D2.1 (K), J3.5, Q3.2 (S)
/BEACON_EN: R36.2, U3.16 (IO13)
/CTD_RX: J3.2, U3.10 (IO7)
/CTD_TX: J3.3, U3.9 (IO6)
/D+: J8.A6 (D+), J8.B6 (D+), U13.1 (I/O1)
/D-: J8.A7 (D-), J8.B7 (D-), U13.3 (I/O2)
/DIP1: SW3.1, U3.40 (IO46)
/DIP2: SW3.2, U3.39 (IO45)
/DIP3: SW3.3, U3.38 (RXD0)
/DIP4: SW3.4, U3.37 (TXD0)
/EN: C6.2, C16.2, R6.1, SW1.1, U3.41 (EN)
/GPS_INT: U3.15 (IO12), U7.4 (EXTINT)
/IMU_SCL_1V8: R13.1, U4.23 (SCL/SCLK), U10.3 (SCL1)
/IMU_SDA_1V8: R12.1, U4.24 (SDA/SDI), U10.4 (SDA1)
/IO0: C10.2, SW2.1, U3.3 (IO0)
/LEAK+: J5.8, R32.2
/LEAK_DET: Q2.2 (E), R34.2, U3.20 (IO17)
/MISO: J9.7 (DAT0), J10.1, R20.2, U3.35 (IO41), U9.8 (MISO)
/MODEM_READY: J4.4, U3.6 (IO3)
/MODEM_RX: J4.2, U3.8 (IO5)
/MODEM_TX: J4.3, U3.7 (IO4)
/MOSI: J9.3 (CMD), J10.2, R26.2, U3.33 (IO39), U9.7 (MOSI)
/MOTOR_DIR: J6.6, U3.28 (IO34)
/MOTOR_EN: J6.7, U3.29 (IO35)
/MOTOR_SPEED: J6.5, U3.27 (IO33)
/RAD_BUSY: U9.3 (BUSY)
/RAD_CS: U3.31 (IO37), U9.9 (NSS)
/RREF+: J5.1, U3.25 (IO26)
/RSENSE+: J5.2, U3.24 (IO21)
/SCK: J9.5 (CLK), R23.2, U3.34 (IO40), U9.6 (SCK)
/SD_CS: J9.2 (DAT3/CD), R27.2, U3.32 (IO38)
/SENSOR_EXTRA1: J7.2
/SENSOR_EXTRA2: J7.4
/SENSOR_SCL: J7.3, U3.4 (IO1)
/SENSOR_SDA: J7.1, U3.5 (IO2)
/SOL_EN: R29.2, U3.17 (IO14)
/SOL_OUT: D1.1 (K), J6.8, Q1.2 (S)
/SX-NRESET: U9.2 (SX-NRESET)
/TURN_ON: J5.6, R39.1, U3.11 (IO8)
/USB_D+: C14.2, R4.2, U13.6 (I/O1)
/USB_D-: C15.1, R5.2, U13.4 (I/O2)
/~GPS_RESET: U3.12 (IO9), U7.8 (~RESET)
GND: BT1.2 (-), C1.2, C2.2, C3.1, C4.2, C5.1, C6.1, C7.2, C8.2, C9.2, C10.1, C11.2, C12.2, C13.2, C14.1, C15.2, C16.1, C17.2, C18.2, C19.2, C21.2, C22.2, C23.2, C24.2, C25.1, C26.2, C27.2, C29.2, C31.2, C33.1, C34.1, C36.1, C37.1, C38.1, C41.1, C42.1, C43.1, C44.2, D1.2 (A), D2.2 (A), FB1.1, H1.1, H2.1, H3.1, J1.2 (Ext), J2.5, J2.6, J3.4, J3.8, J4.8, J5.3, J5.4, J5.7, J6.4, J7.5, J7.6, J8.A1 (GND), J8.A12 (GND), J8.B1 (GND), J8.B12 (GND), J9.6 (VSS), J9.9 (SHIELD), JP2.1 (A), R2.1, R9.1, R18.1, R22.1, R24.2, R25.1, R34.1, R39.2, SW1.2, SW2.2, SW3.5, SW3.6, SW3.7, SW3.8, U1.2 (GND), U2.3 (CMP1), U2.5 (GND), U2.10 (CMP2), U2.13 (EPAD), U3.1 (GND), U3.26 (GND), U3.42 (GND), U3.43 (EPAD), U4.18 (GND), U4.20 (GND), U5.5 (~EN), U5.17 (GND), U6.3 (CMP1), U6.5 (GND), U6.10 (CMP2), U6.13 (EPAD), U7.7 (VDD_USB), U7.10 (GND), U7.12 (GND), U7.13 (GND), U7.24 (GND), U8.1 (GND), U8.7 (GND), U9.10 (GND), U10.1 (GND), U11.1 (GND), U12.1 (GND), U13.2 (GND), U14.2, U14.3, U15.2, U15.3
unnamed: BT1.1 (+), U2.12 (V2)
unnamed: C4.1, U3.18 (IO15), Y1.1
unnamed: C5.2, U3.19 (IO16), Y1.2
unnamed: C13.1, U4.10 (REGOUT)
unnamed: C25.2, F1.2, U5.7 (SENSE), U5.8 (OUT), U5.9 (OUT)
unnamed: C27.1, F2.2, U6.9 (Out)
unnamed: C35.1, U11.6 (VBST)
unnamed: C35.2, L3.1, U11.2 (SW)
unnamed: C36.2, C37.2, F3.2, L3.2, R17.1
unnamed: C39.1, L4.1, U12.2 (SW)
unnamed: C39.2, U12.6 (BOOT)
unnamed: C40.1, C41.2, C43.2, F4.2, L4.2, R21.1
unnamed: C40.2, R21.2, R22.2, U12.4 (FB)
unnamed: C42.2, FB1.2, J8.S1 (SHIELD)
unnamed: C44.1, FB2.2, J8.A4 (VBUS), J8.A9 (VBUS), J8.B4 (VBUS), J8.B9 (VBUS), U13.5 (VBUS)
unnamed: J1.1 (In), U7.11 (RF_IN)
unnamed: J8.A5 (CC1), R24.1
unnamed: J8.B5 (CC2), R25.2
unnamed: L1.1, U1.5 (SW)
unnamed: Q1.1 (G), R31.1
unnamed: Q2.1 (B), R32.1, R33.1
unnamed: Q3.1 (G), R38.1
unnamed: R1.2, R2.2, U2.4 (ADJ)
unnamed: R3.1, U3.21 (IO18)
unnamed: R4.1, U3.23 (IO20)
unnamed: R5.1, U3.22 (IO19)
unnamed: R8.2, R9.2, U6.4 (ADJ)
unnamed: R14.1, U10.7 (VREF2), U10.8 (EN)
unnamed: R17.2, R18.2, U11.4 (VFB)
unnamed: R29.1, U14.1
unnamed: R30.2, R31.2, U14.4
unnamed: R36.1, U15.1
unnamed: R37.2, R38.2, U15.4
unnamed: U8.2 (CSB), U8.6 (VDDIO)
VBUS: C18.1, FB2.1, R8.1, U6.1 (V1)

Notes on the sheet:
External Launch Switch VCC Switch On/Off
I2C Data Bus
Components on back of board
SCL Bus
Devices on 3V3 Backup Battery
USBC 2.0 Connector
Power Source Switching
I don't think these should both be pin 7
Light Beacon Power 12 V GND
Battery Controller Power + Power - I2C SCL I2C SDA
1V8 <-> 3V3 I2C Conversion
Leak Sensor
Power Conversion
Debug Pins
Connectors
Motor Enable Direction Analog Speed
Acoustic Modem Power 12-36V GND Ready RS232 Rx RS232 Tx
GPS: NEO-M9N
5V_BATT is also converted to 3V3 and sent to the sensor board
Leak Sensor + Leak Sensor -
SPI Data Bus
IMU
This is on 3V3BCKP mostly for routing purposes
Temperature, Humidity, Pressure Sensor
12V Solenoid and Beacon Control
3.3V Battery Backup Switching Only for MCU, GPS, and Radio
Solenoid Enable
Liquid Level Sense+ Sense- Ref+ Ref-
Radio: LoRa LR62E
3V3 -> 1V8
MCU: ESP32-S2
5V -> 3V3
CTD Power 5V RS232 4V Rx RS232 4V Tx GND
MicroSD Card Reader
VBat -> 12V
IMU 1V8 <-> 3V3 I2C Conversion
VBat -> 5V
Solenoid and Beacon must not be run simultaneously
5V USB Switching This rail is used only within the control board
SDA Bus

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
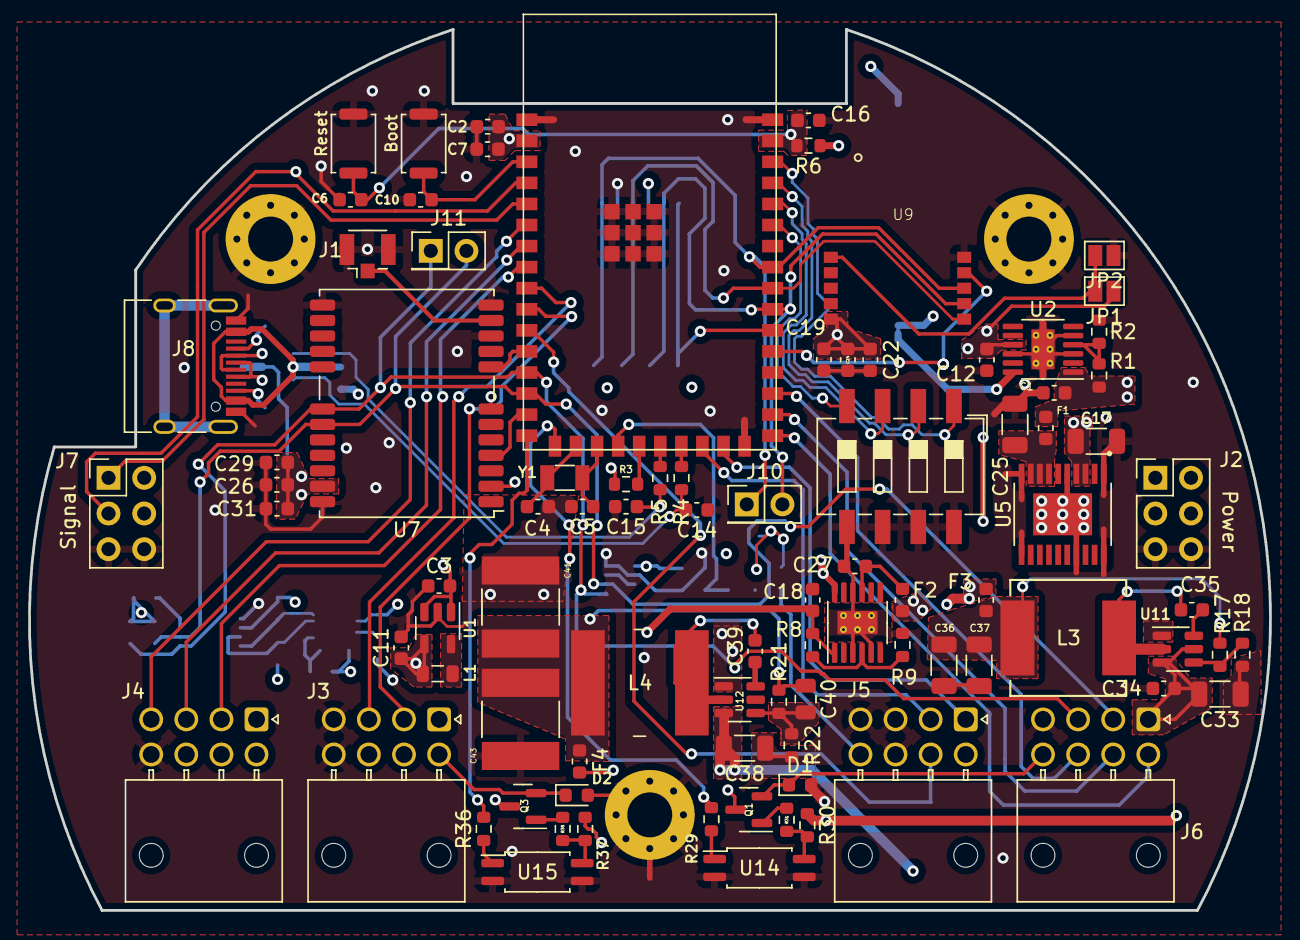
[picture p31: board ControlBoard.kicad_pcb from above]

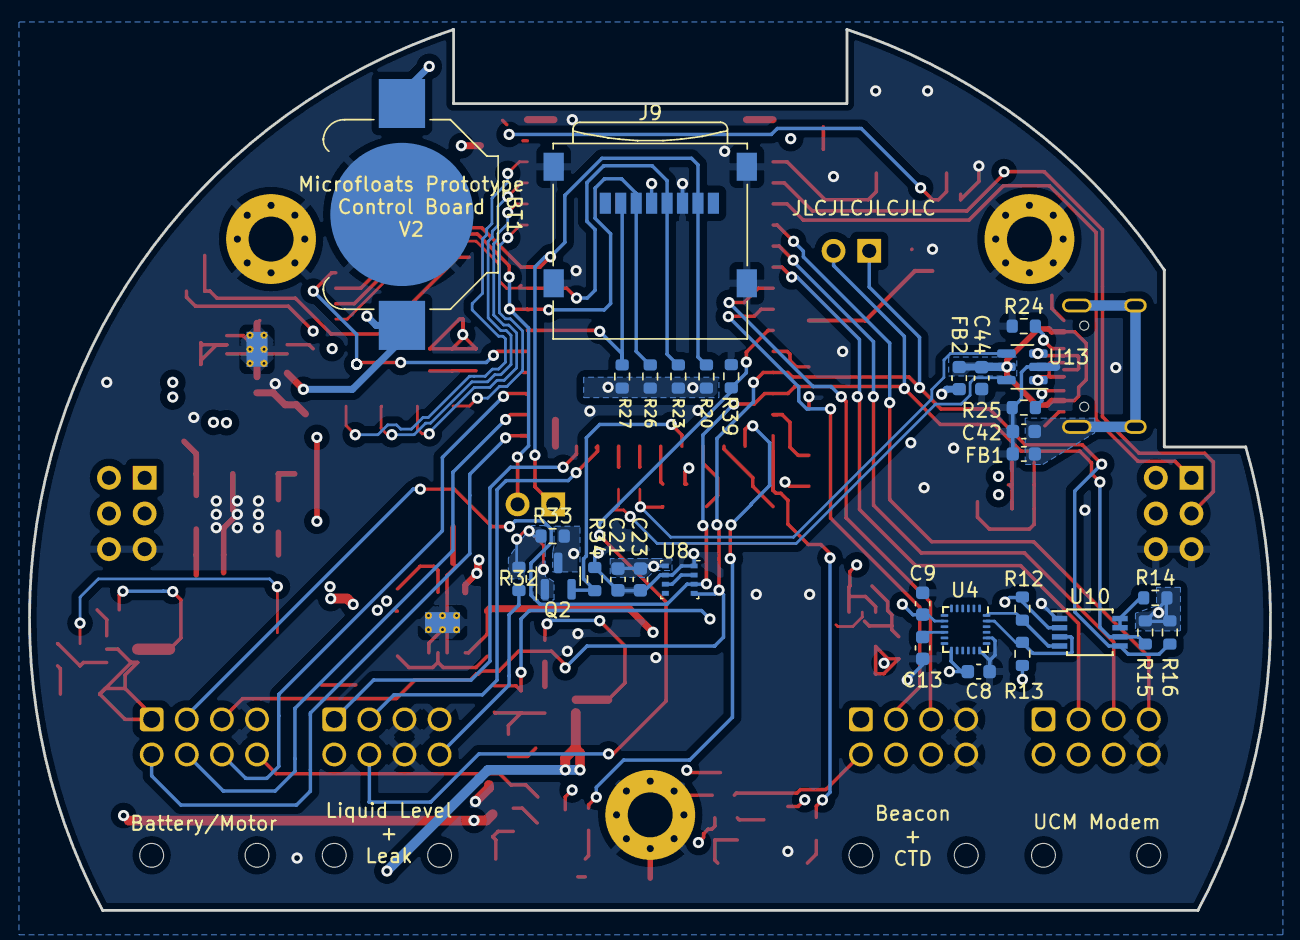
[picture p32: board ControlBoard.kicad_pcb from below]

Board: 4 copper layers, 88.4 x 62.7 mm, 123 parts (31 on the bottom side), 84 nets.

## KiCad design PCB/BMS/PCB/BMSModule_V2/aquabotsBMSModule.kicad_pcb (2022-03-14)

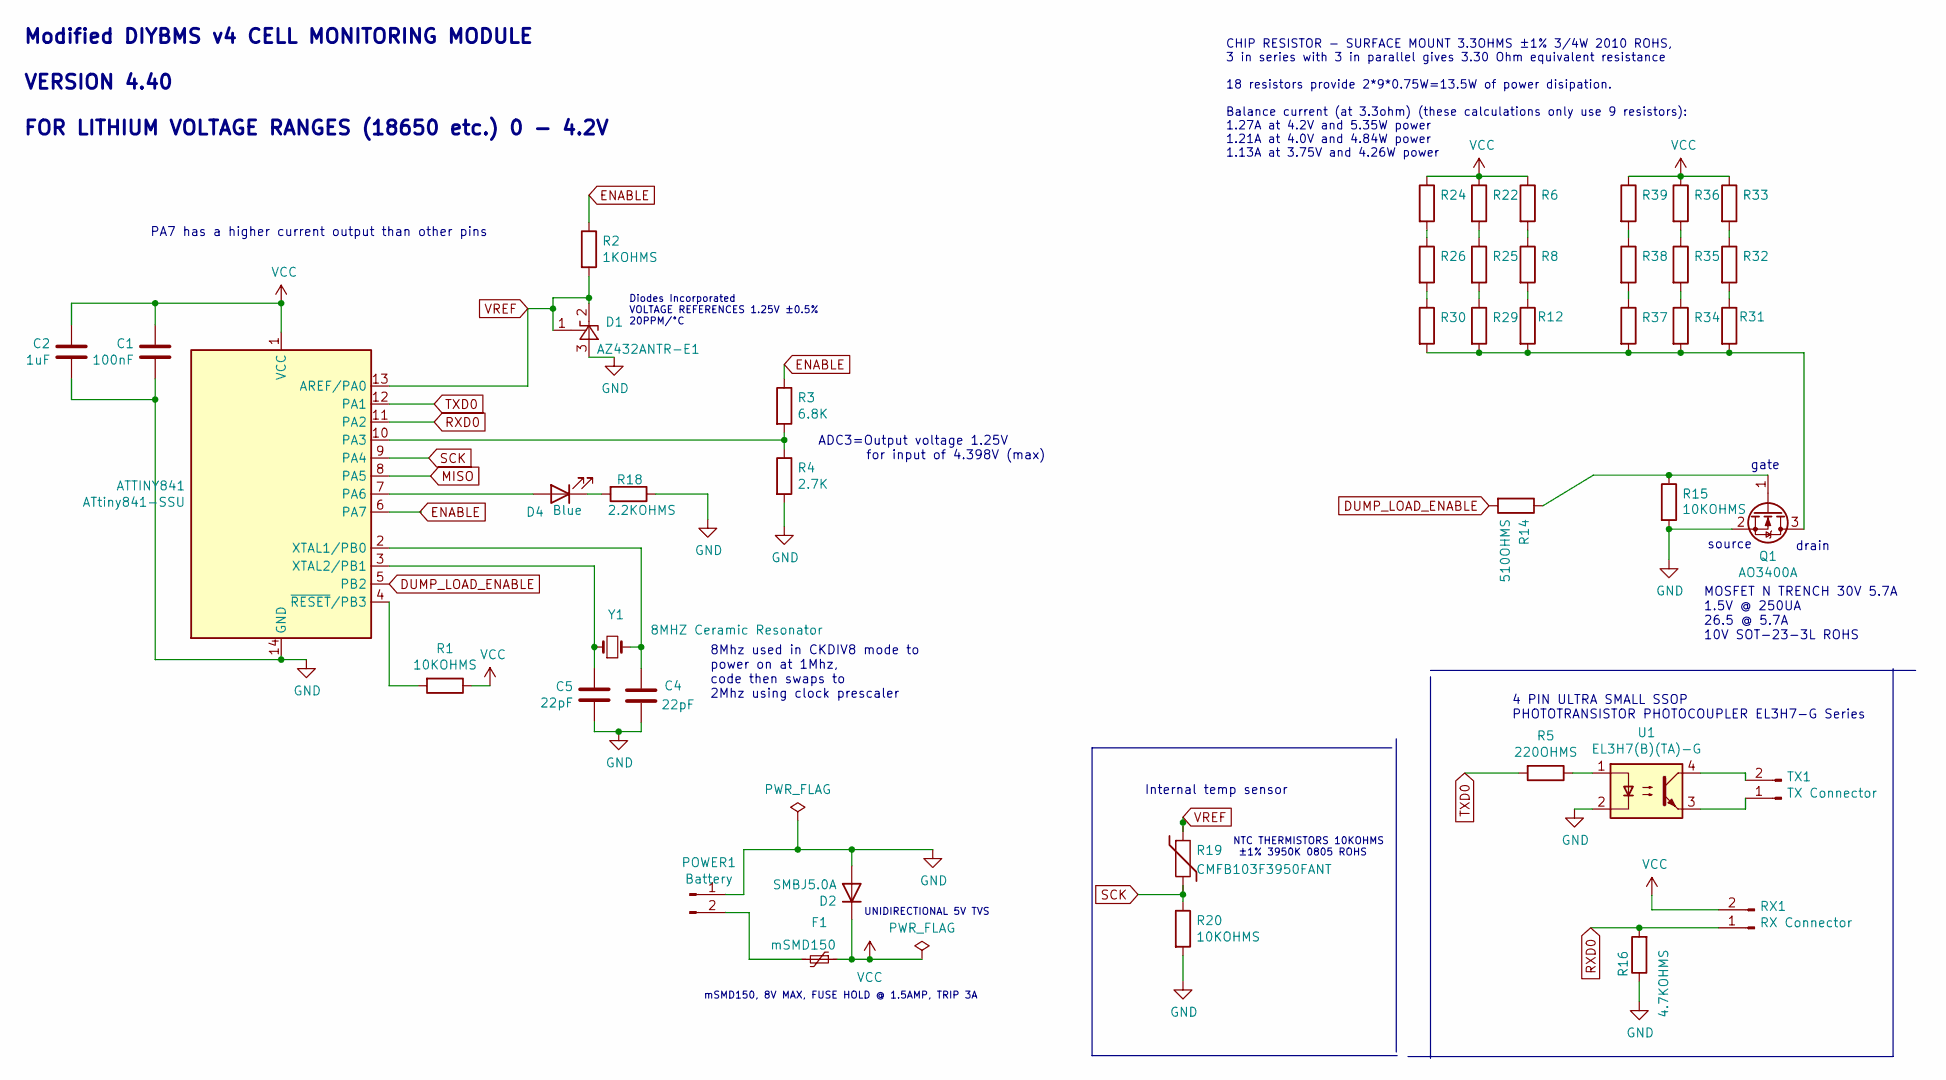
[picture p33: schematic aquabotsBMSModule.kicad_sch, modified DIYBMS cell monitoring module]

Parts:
ATTINY841: ATtiny841-SSU; SOIC-14_3.9x8.7mm_P1.27mm; LCSCStockCode C219103
C1: 100nF; C_0805_2012Metric; PartNumber CC0805KRX7R9BB104; LCSCStockCode C49678
C2: 1uF; C_0805_2012Metric; PartNumber CL21B105KBFNNNE; LCSCStockCode C28323
C4, C5: 22pF; C_0805_2012Metric; PartNumber CL21C220JBANNNC; LCSCStockCode C1804
D1: AZ432ANTR-E1; SOT-23; PartNumber AZ432ANTR-E1; LCSCStockCode C84139
D2: SMBJ5.0A; D_SMB; LCSCStockCode C440263
D4: Blue; LED_0805_2012Metric; PartNumber Blue LED; LCSCStockCode C2293
F1: mSMD150; Fuse_1812_4532Metric; PartNumber mSMD150; LCSCStockCode C70121
POWER1: Battery; JST_PH_S2B-PH-K_1x02_P2.00mm_Horizontal; PartNumber S2B-PH-K(LF)(SN); LCSCStockCode C265016
Q1: AO3400A; SOT-23; PartNumber AO3400A; LCSCStockCode C20917
R1, R15, R20: 10KOHMS; R_0805_2012Metric; PartNumber 0805W8F1002T5E; LCSCStockCode C17414
R2: 1KOHMS; R_0805_2012Metric; PartNumber 0805W8F1001T5E; LCSCStockCode C17513
R3: 6.8K; R_0805_2012Metric; PartNumber 0805W8F6801T5E; LCSCStockCode C17772
R4: 2.7K; R_0805_2012Metric; PartNumber 0805W8F2701T5E; LCSCStockCode C17530
R5: 220OHMS; R_0805_2012Metric; PartNumber 0805W8F2200T5E; LCSCStockCode C17557
R6, R8, R12, R22, R24, R25, R26, R29, R30, R31, R32, R33, R34, R35, R36, R37, R38, R39: 3.3OHM 3/4W; R_2010_5025Metric; PartNumber 201007F330KT4E; LCSCStockCode C270971
R14: 510OHMS; R_0805_2012Metric; PartNumber 0805W8F5100T5E; LCSCStockCode C17734
R16: 4.7KOHMS; R_0805_2012Metric; PartNumber 0805W8F4701T5E; LCSCStockCode C17673
R18: 2.2KOHMS; R_0805_2012Metric; PartNumber 0805W8F2201T5E; LCSCStockCode C17520
R19: CMFB103F3950FANT; R_0805_2012Metric; PartNumber CMFB103F3950FANT; LCSCStockCode C51597
RX1: RX Connector; JST_PH_S2B-PH-K_1x02_P2.00mm_Horizontal; PartNumber S2B-PH-K(LF)(SN); LCSCStockCode C265016
TX1: TX Connector; JST_PH_S2B-PH-K_1x02_P2.00mm_Horizontal; PartNumber S2B-PH-K(LF)(SN); LCSCStockCode C265016
U1: EL3H7(B)(TA)-G; SOP-4_4.4x2.6mm_P1.27mm; PartNumber EL3H7(B)(TA)-G; LCSCStockCode C32565
Y1: 8MHZ Ceramic Resonator; Crystal_SMD_5032-2Pin_5.0x3.2mm; PartNumber X50328MSB2GI; LCSCStockCode C115962

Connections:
DUMP_LOAD_ENABLE: ATTINY841.5 (PB2), R14.2
ENABLE: ATTINY841.6 (PA7), R2.1, R3.1
GND: ATTINY841.14 (GND), C1.2, C2.2, C4.2, C5.2, D1.3 (A), D2.2 (A), POWER1.1, Q1.2 (S), R4.2, R15.2, R16.1, R18.1, R20.2, U1.2
MISO: ATTINY841.8 (PA5)
unnamed: ATTINY841.2 (XTAL1/PB0), C4.1, Y1.2
unnamed: ATTINY841.3 (XTAL2/PB1), C5.1, Y1.1
unnamed: ATTINY841.4 (~RESET/PB3), R1.2
unnamed: ATTINY841.7 (PA6), D4.2 (A)
unnamed: ATTINY841.10 (PA3), R3.2, R4.1
unnamed: D4.1 (K), R18.2
unnamed: F1.2, POWER1.2
unnamed: Q1.1 (G), R14.1, R15.1
unnamed: Q1.3 (D), R12.2, R29.2, R30.2, R31.2, R34.2, R37.2
unnamed: R5.1, U1.1
unnamed: R6.2, R8.1
unnamed: R8.2, R12.1
unnamed: R22.2, R25.1
unnamed: R24.2, R26.1
unnamed: R25.2, R29.1
unnamed: R26.2, R30.1
unnamed: R31.1, R32.2
unnamed: R32.1, R33.2
unnamed: R34.1, R35.2
unnamed: R35.1, R36.2
unnamed: R37.1, R38.2
unnamed: R38.1, R39.2
unnamed: TX1.1, U1.3
unnamed: TX1.2, U1.4
RXD0: ATTINY841.11 (PA2), R16.2, RX1.1
SCK: ATTINY841.9 (PA4), R19.2, R20.1
TXD0: ATTINY841.12 (PA1), R5.2
VCC: ATTINY841.1 (VCC), C1.1, C2.1, D2.1 (K), F1.1, R1.1, R6.1, R22.1, R24.1, R33.1, R36.1, R39.1, RX1.2
VREF: ATTINY841.13 (AREF/PA0), D1.1 (FB), D1.2 (K), R2.2, R19.1

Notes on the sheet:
UNIDIRECTIONAL 5V TVS
Internal temp sensor
CHIP RESISTOR - SURFACE MOUNT 3.3OHMS ±1% 3/4W 2010 ROHS, 3 in series with 3 in parallel gives 3.30 Ohm equivalent resistance 18 resistors provide 2*9*0.75W=13.5W of power disipation. Balance current (at 3.3ohm) (these calculations only use 9 resistors): 1.27A at 4.2V and 5.35W power 1.21A at 4.0V 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
mSMD150, 8V MAX, FUSE HOLD @ 1.5AMP, TRIP 3A
Diodes Incorporated VOLTAGE REFERENCES 1.25V ±0.5% 20PPM/°C
8Mhz used in CKDIV8 mode to power on at 1Mhz, code then swaps to 2Mhz using clock prescaler
NTC THERMISTORS 10KOHMS ±1% 3950K 0805 ROHS
ADC3=Output voltage 1.25V for input of 4.398V (max)
gate
Modified DIYBMS v4 CELL MONITORING MODULE VERSION 4.40 FOR LITHIUM VOLTAGE RANGES (18650 etc.) 0 - 4.2V
PA7 has a higher current output than other pins
source
4 PIN ULTRA SMALL SSOP PHOTOTRANSISTOR PHOTOCOUPLER EL3H7-G Series
MOSFET N TRENCH 30V 5.7A 1.5V @ 250UA 26.5 @ 5.7A 10V SOT-23-3L ROHS
drain

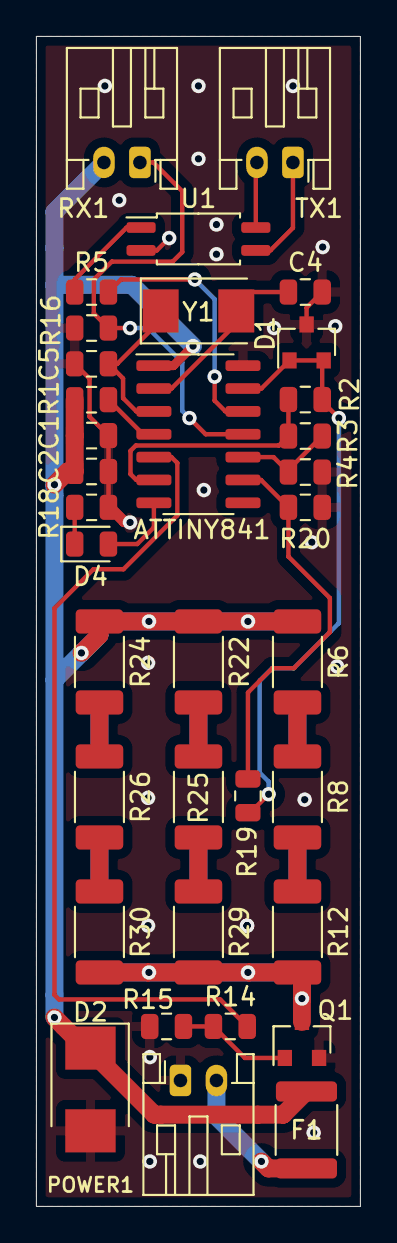
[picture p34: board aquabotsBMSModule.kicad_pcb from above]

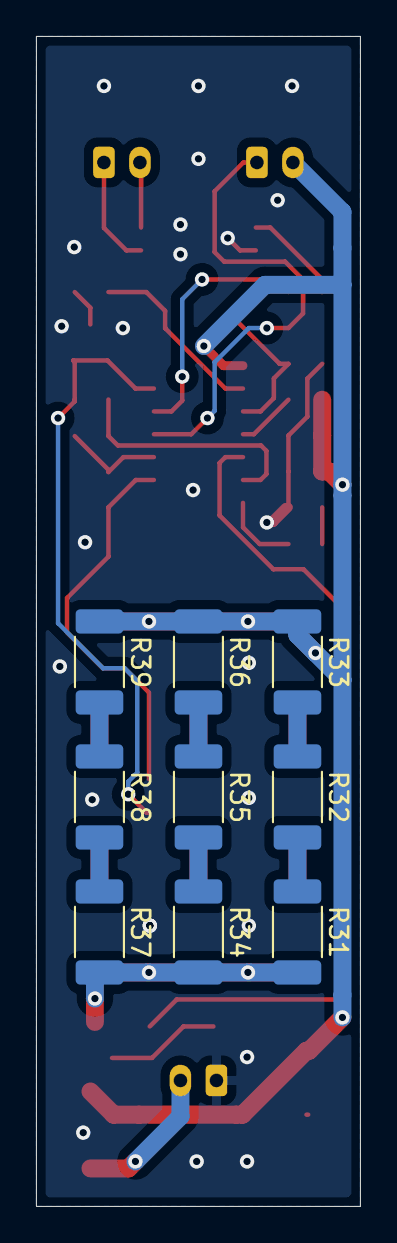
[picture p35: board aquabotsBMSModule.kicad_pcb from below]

Board: 2 copper layers, 18.0 x 65.0 mm, 44 parts (9 on the bottom side), 32 nets.

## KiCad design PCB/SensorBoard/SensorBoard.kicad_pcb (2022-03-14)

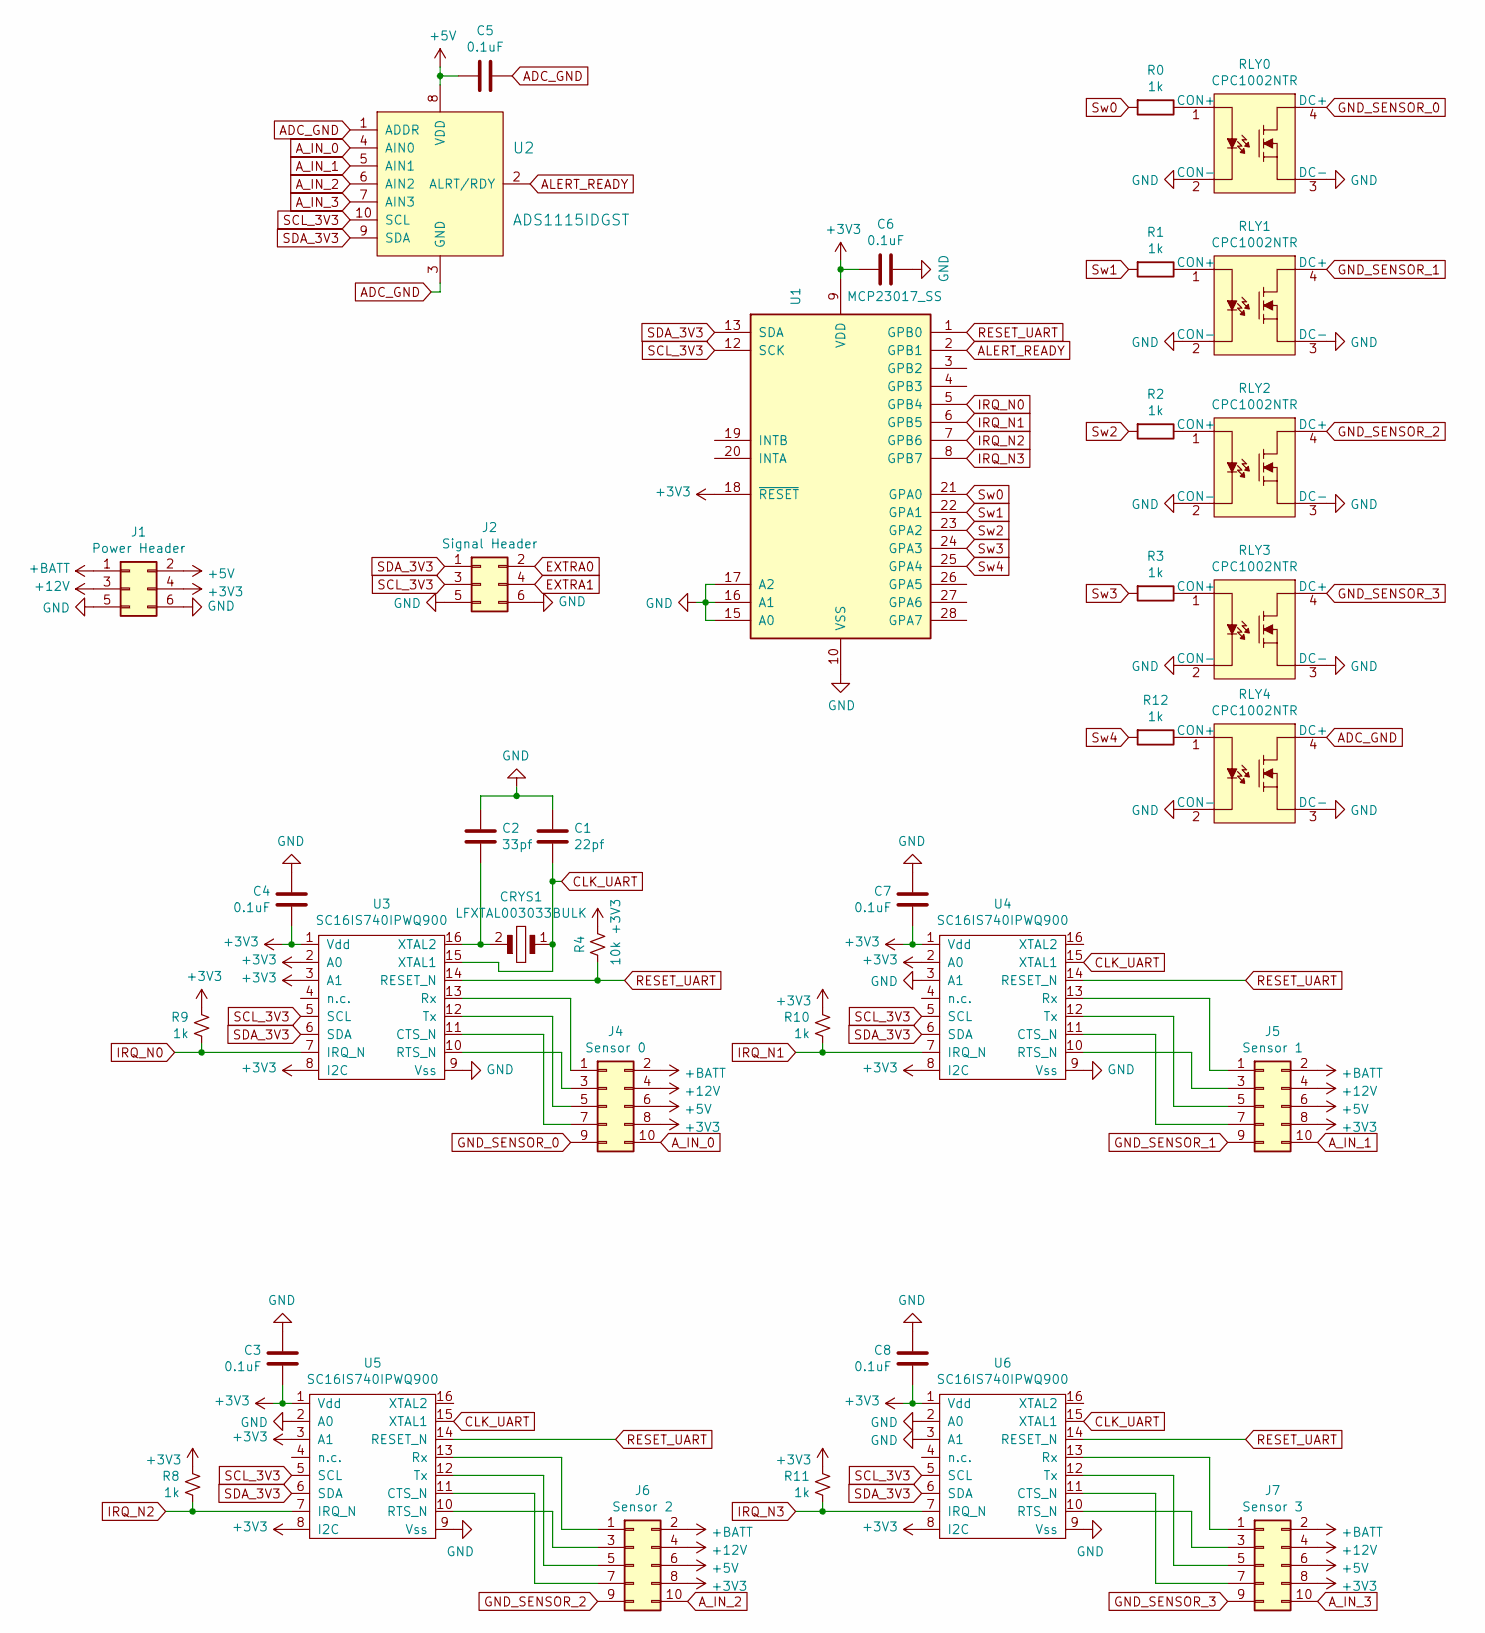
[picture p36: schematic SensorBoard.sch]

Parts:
C1: 22pf; C_0603_1608Metric_Pad1.05x0.95mm_HandSolder
C2: 33pf; C_0603_1608Metric_Pad1.05x0.95mm_HandSolder
C3, C4, C5, C6, C7, C8: 0.1uF; C_0603_1608Metric_Pad1.05x0.95mm_HandSolder
CRYS1: LFXTAL003033BULK; Crystal_HC49-U_Vertical
J1: Power Header; PinHeader_2x03_P2.54mm_Vertical
J2: Signal Header; PinHeader_2x03_P2.54mm_Vertical
J4: Sensor 0; Molex_Nano-Fit_105314-xx10_2x05_P2.50mm_Horizontal
J5: Sensor 1; Molex_Nano-Fit_105314-xx10_2x05_P2.50mm_Horizontal
J6: Sensor 2; Molex_Nano-Fit_105314-xx10_2x05_P2.50mm_Horizontal
J7: Sensor 3; Molex_Nano-Fit_105314-xx10_2x05_P2.50mm_Horizontal
R0, R1, R2, R3, R8, R9, R10, R11, R12: 1k; R_0805_2012Metric_Pad1.15x1.40mm_HandSolder
R4: 10k; R_0805_2012Metric_Pad1.15x1.40mm_HandSolder
RLY0, RLY1, RLY2, RLY3, RLY4: CPC1002NTR; SOP-4_3.8x4.1mm_P2.54mm; MPN CPC1002NTR; Digi-Key_PN CLA230CT-ND
U1: MCP23017_SS; SSOP-28_5.3x10.2mm_P0.65mm
U2: ADS1115IDGST; VSSOP-10_3x3mm_P0.5mm; MPN ADS1115IDGST; Digi-Key_PN 296-24934-1-ND
U3, U4, U5, U6: SC16IS740IPWQ900; TSSOP-16_4.4x5mm_P0.65mm

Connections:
+3V3: C3.2, C4.2, C6.2, C7.2, C8.2, J1.4, J4.8, J5.8, J6.8, J7.8, R4.2, R8.2, R9.2, R10.2, R11.2, U1.9 (VDD), U1.18 (~RESET~), U3.1 (Vdd), U3.2 (A0), U3.3 (A1), U3.8 (I2C), U4.1 (Vdd), U4.2 (A0), U4.8 (I2C), U5.1 (Vdd), U5.3 (A1), U5.8 (I2C), U6.1 (Vdd), U6.8 (I2C)
+5V: C5.2, J1.2, J4.6, J5.6, J6.6, J7.6, U2.8 (VDD)
+12V: J1.3, J4.4, J5.4, J6.4, J7.4
+BATT: J1.1, J4.2, J5.2, J6.2, J7.2
ADC_GND: C5.1, RLY4.4 (DC+), U2.1 (ADDR), U2.3 (GND)
ALERT_READY: U1.2 (GPB1), U2.2 (ALRT/RDY)
A_IN_0: J4.10, U2.4 (AIN0)
A_IN_1: J5.10, U2.5 (AIN1)
A_IN_2: J6.10, U2.6 (AIN2)
A_IN_3: J7.10, U2.7 (AIN3)
CLK_UART: C1.2, CRYS1.1, U3.15 (XTAL1), U4.15 (XTAL1), U5.15 (XTAL1), U6.15 (XTAL1)
EXTRA0: J2.2
EXTRA1: J2.4
GND: C1.1, C2.1, C3.1, C4.1, C6.1, C7.1, C8.1, J1.5, J1.6, J2.5, J2.6, RLY0.2 (CON-), RLY0.3 (DC-), RLY1.2 (CON-), RLY1.3 (DC-), RLY2.2 (CON-), RLY2.3 (DC-), RLY3.2 (CON-), RLY3.3 (DC-), RLY4.2 (CON-), RLY4.3 (DC-), U1.10 (VSS), U1.15 (A0), U1.16 (A1), U1.17 (A2), U3.9 (Vss), U4.3 (A1), U4.9 (Vss), U5.2 (A0), U5.9 (Vss), U6.2 (A0), U6.3 (A1), U6.9 (Vss)
GND_SENSOR_0: J4.9, RLY0.4 (DC+)
GND_SENSOR_1: J5.9, RLY1.4 (DC+)
GND_SENSOR_2: J6.9, RLY2.4 (DC+)
GND_SENSOR_3: J7.9, RLY3.4 (DC+)
IRQ_N0: R9.1, U1.5 (GPB4), U3.7 (IRQ_N)
IRQ_N1: R10.1, U1.6 (GPB5), U4.7 (IRQ_N)
IRQ_N2: R8.1, U1.7 (GPB6), U5.7 (IRQ_N)
IRQ_N3: R11.1, U1.8 (GPB7), U6.7 (IRQ_N)
unnamed: C2.2, CRYS1.2, U3.16 (XTAL2)
unnamed: J4.1, U3.13 (Rx)
unnamed: J4.3, U3.10 (RTS_N)
unnamed: J4.5, U3.12 (Tx)
unnamed: J4.7, U3.11 (CTS_N)
unnamed: J5.1, U4.13 (Rx)
unnamed: J5.3, U4.10 (RTS_N)
unnamed: J5.5, U4.12 (Tx)
unnamed: J5.7, U4.11 (CTS_N)
unnamed: J6.1, U5.13 (Rx)
unnamed: J6.3, U5.10 (RTS_N)
unnamed: J6.5, U5.12 (Tx)
unnamed: J6.7, U5.11 (CTS_N)
unnamed: J7.1, U6.13 (Rx)
unnamed: J7.3, U6.10 (RTS_N)
unnamed: J7.5, U6.12 (Tx)
unnamed: J7.7, U6.11 (CTS_N)
unnamed: R0.1, RLY0.1 (CON+)
unnamed: R1.1, RLY1.1 (CON+)
unnamed: R2.1, RLY2.1 (CON+)
unnamed: R3.1, RLY3.1 (CON+)
unnamed: R12.1, RLY4.1 (CON+)
RESET_UART: R4.1, U1.1 (GPB0), U3.14 (RESET_N), U4.14 (RESET_N), U5.14 (RESET_N), U6.14 (RESET_N)
SCL_3V3: J2.3, U1.12 (SCK), U2.10 (SCL), U3.5 (SCL), U4.5 (SCL), U5.5 (SCL), U6.5 (SCL)
SDA_3V3: J2.1, U1.13 (SDA), U2.9 (SDA), U3.6 (SDA), U4.6 (SDA), U5.6 (SDA), U6.6 (SDA)
Sw0: R0.2, U1.21 (GPA0)
Sw1: R1.2, U1.22 (GPA1)
Sw2: R2.2, U1.23 (GPA2)
Sw3: R3.2, U1.24 (GPA3)
Sw4: R12.2, U1.25 (GPA4)

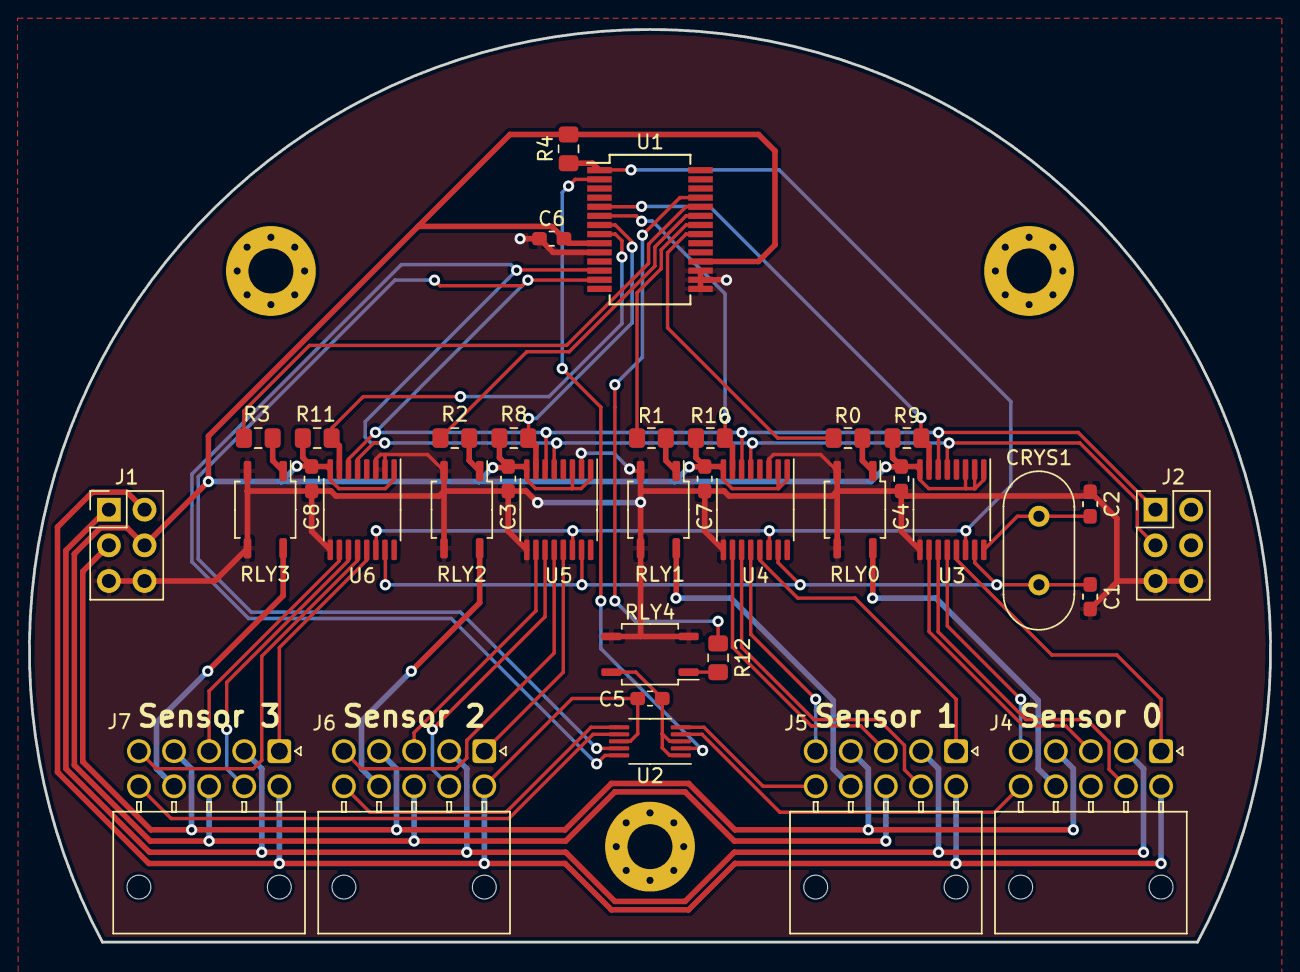
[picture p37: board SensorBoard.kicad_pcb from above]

Board: 2 copper layers, 88.4 x 65.0 mm, 36 parts (0 on the bottom side), 50 nets.

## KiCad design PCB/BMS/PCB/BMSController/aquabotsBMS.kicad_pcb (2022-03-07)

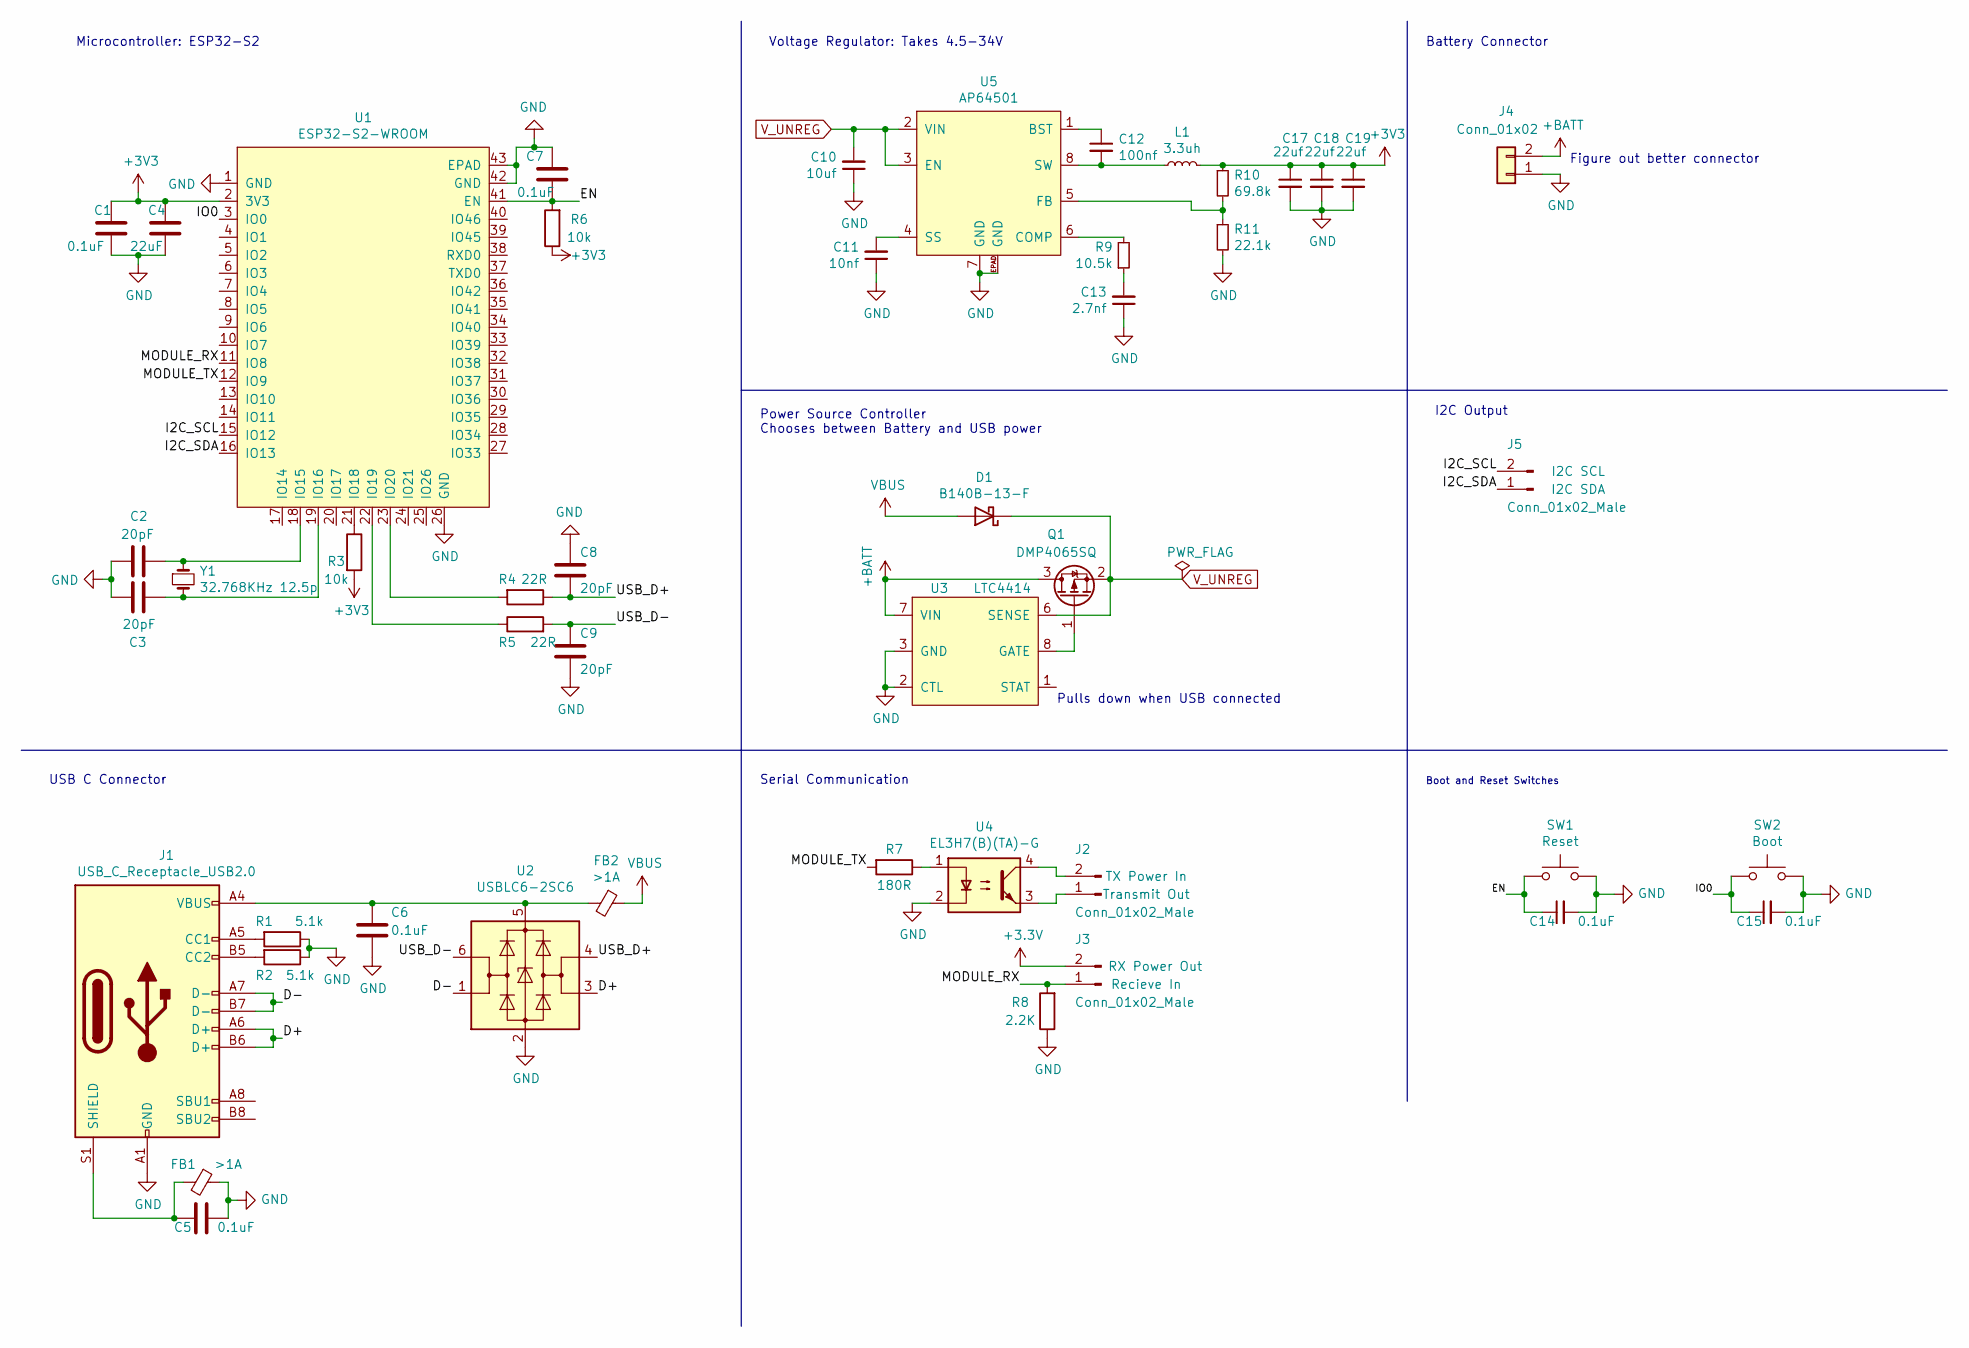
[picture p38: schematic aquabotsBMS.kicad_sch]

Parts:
C1, C5, C6, C7, C14, C15: 0.1uF; C_0603_1608Metric
C2, C3, C8, C9: 20pF; C_0603_1608Metric
C4: 22uF; C_0603_1608Metric
C10: 10uf; C_1206_3216Metric
C11: 10nf; C_0603_1608Metric
C12: 100nf; C_0603_1608Metric
C13: 2.7nf; C_0603_1608Metric
C17, C18, C19: 22uf; C_1206_3216Metric
D1: B140B-13-F; D_SMA
FB1, FB2: >1A; L_0603_1608Metric
J1: USB_C_Receptacle_USB2.0; USB_C_Receptacle_HRO_TYPE-C-31-M-12
J2, J3, J5: Conn_01x02_Male; JST_PH_S2B-PH-K_1x02_P2.00mm_Horizontal
J4: Conn_01x02; PinHeader_1x02_P2.54mm_Vertical
L1: 3.3uh; L_Wuerth_HCI-1050
Q1: DMP4065SQ; SOT-23
R1, R2: 5.1k; R_0603_1608Metric
R3, R6: 10k; R_0603_1608Metric
R4, R5: 22R; R_0603_1608Metric
R7: 180R; R_0603_1608Metric
R8: 2.2K; R_0603_1608Metric; LCSCStockCode C17520
R9: 10.5k; R_0603_1608Metric
R10: 69.8k; R_0603_1608Metric
R11: 22.1k; R_0603_1608Metric
SW1: Reset; SW_Push_SPST_NO_Alps_SKRK
SW2: Boot; SW_Push_SPST_NO_Alps_SKRK
U1: ESP32-S2-WROOM
U2: USBLC6-2SC6; SOT-23-6
U3: LTC4414; MSOP-8_3x3mm_P0.65mm
U4: EL3H7(B)(TA)-G; SOP-4_4.4x2.6mm_P1.27mm; LCSCStockCode C32565
U5: AP64501; AP64501SP-13
Y1: 32.768KHz 12.5p; Crystal_SMD_3215-2Pin_3.2x1.5mm

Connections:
+BATT: J4.2, Q1.3 (D), U3.7 (VIN)
/D+: J1.A6 (D+), J1.B6 (D+), U2.3 (I/O2)
/D-: J1.A7 (D-), J1.B7 (D-), U2.1 (I/O1)
/EN: C7.2, C14.1, R6.2, SW1.1, U1.41 (EN)
/I2C_SCL: J5.2, U1.15 (IO12)
/I2C_SDA: J5.1, U1.16 (IO13)
/IO0: C15.1, SW2.1, U1.3 (IO0)
/MODULE_RX: J3.1, R8.2, U1.11 (IO8)
/MODULE_TX: R7.2, U1.12 (IO9)
/USB_D+: C8.2, R4.1, U2.4 (I/O2)
/USB_D-: C9.1, R5.2, U2.6 (I/O1)
GND: C1.2, C2.2, C3.1, C4.2, C5.2, C6.2, C7.1, C8.1, C9.2, C10.1, C11.1, C13.1, C14.2, C15.2, C17.2, C18.2, C19.2, FB1.1, J1.A1 (GND), J1.A12 (GND), J1.B1 (GND), J1.B12 (GND), J4.1, R1.1, R2.1, R8.1, R11.2, SW1.2, SW2.2, U1.1 (GND), U1.26 (GND), U1.42 (GND), U1.43 (EPAD), U2.2 (GND), U3.2 (CTL), U3.3 (GND), U4.2, U5.7 (GND), U5.EPAD (GND)
unnamed: C2.1, U1.18 (IO15), Y1.1
unnamed: C3.2, U1.19 (IO16), Y1.2
unnamed: C5.1, FB1.2, J1.S1 (SHIELD)
unnamed: C6.1, FB2.2, J1.A4 (VBUS), J1.A9 (VBUS), J1.B4 (VBUS), J1.B9 (VBUS), U2.5 (VBUS)
unnamed: C11.2, U5.4 (SS)
unnamed: C12.1, U5.1 (BST)
unnamed: C12.2, L1.1, U5.8 (SW)
unnamed: C13.2, R9.1
unnamed: J1.A5 (CC1), R1.2
unnamed: J1.B5 (CC2), R2.2
unnamed: J2.1, U4.3
unnamed: J2.2, U4.4
unnamed: Q1.1 (G), U3.8 (GATE)
unnamed: R3.1, U1.21 (IO18)
unnamed: R4.2, U1.23 (IO20)
unnamed: R5.1, U1.22 (IO19)
unnamed: R7.1, U4.1
unnamed: R9.2, U5.6 (COMP)
unnamed: R10.2, R11.1, U5.5 (FB)
VBUS: D1.2 (A), FB2.1
V_UNREG: C10.2, D1.1 (K), Q1.2 (S), U3.6 (SENSE), U5.2 (VIN), U5.3 (EN)

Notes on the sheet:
Figure out better connector
I2C Output
Pulls down when USB connected
Serial Communication
Microcontroller: ESP32-S2
Power Source Controller Chooses between Battery and USB power
Voltage Regulator: Takes 4.5-34V
Battery Connector
Boot and Reset Switches
USB C Connector

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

Board: 4 copper layers, 40.0 x 65.0 mm, 47 parts (0 on the bottom side), 34 nets.

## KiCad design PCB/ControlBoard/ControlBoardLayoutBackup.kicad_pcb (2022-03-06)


Board: 2 copper layers, 88.4 x 62.7 mm, 3 parts (0 on the bottom side), 2 nets, no tracks yet.

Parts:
J1: Power Header; PinHeader_2x03_P2.54mm_Vertical
J2: Signal Header; PinHeader_2x03_P2.54mm_Vertical
U3: ESP32-S2-WROOM

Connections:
+3V3: J1.4, U3.2
GND: J1.5, J1.6, J2.5, J2.6, U3.1, U3.26, U3.42, U3.43

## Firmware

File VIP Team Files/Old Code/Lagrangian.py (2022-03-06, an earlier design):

### TODO: update to use correct method of toggling GPIO pins
###       add correct pins for i2c and update remaining code to use it for all analog signals
import RPi.GPIO as GPIO
from smbus2 import SMBus
import time
import socket
from requests import get
import pickle
import struct
#I2C over pins 2 and 3
#    12Bit ADC
#      Hall Effect Sensors 1 and 2
#      Pressure Sensor analog input
#    DAC
#      Motor Speed Analog Out




def readPressure():
	#Read from Pressure Sensor    
	pres = read_adc(2)
 
	#currently assuming this returns the voltage so we need to divide it by the max voltage of the system (5V)
	return pres/5.0

def readBuoyancy():

	# read position of piston from hall sensors and return % buoyancy

	b1 = read_adc(Channel = 1)
	b2 = read_adc(Channel = 0)

	return abs(b1-2.5) * 1/2.5

def read_adc(Channel):
            try:
                config = 0x0003 | 0x8000 | 0x0100 | programmable_gain_map[6144]  | channel_map[Channel] | samples_per_second_map[1600]
                                
                #transmit config info
                bus.write_i2c_block_data(ADC_addr, 1, [(config >> 8) & 0xFF, config & 0xFF]) #write to register 1

                time.sleep(1/1600 + .001) #wait 1 sample

                #read value
                chlist = bus.read_i2c_block_data(ADC_addr, 0, 2) #read 2 bytes from register 0
                voltage =  ((chlist[0] << 4) | chlist[1])  * 6144 / 2048.0 / 1000.0

                num = (200/.5)*voltage - 1000
                if(abs(num)<75 or int(num) == 209 or int(num) == 190 or int(num) == 113 or  int(num) == 132 or int(num) == 94):
                        num = 0.0
                return num
            except:
                return 0.0

def getDepth(preassure):
	#P/(pg) = depth
	depth = preassure/(water_density*grav)
	return depth

def setSolenoidValve(val):
    # Retract if val == 0, extend if val == 1
    if (val == 1 or val == GPIO.HIGH):
        GPIO.output(SVpin, GPIO.HIGH)
    elif (val == 0 or val == GPIO.LOW):
        GPIO.output(SVpin, GPIO.LOW)

def writeVoltage(Vout):
        value  = int((4096*Vout)/5.0)
        if(value > 4095):
                value = 4095
        if(value < 0):
                value = 0 
        reg_data = [(value >> 4) & 0xFF, ((value & 0xF) << 4) & 0xFF]
        #reg_data = [int(value/16), (value % 16) << 4]
      
        bus.write_i2c_block_data(DAC_addr,0x60,reg_data)

def setMotor(enable, direction, rpm):                 
    speedRange = 11285
    rpm = rpm / 100
    rpm = 500 * rpm                                # this if for a 7 pole pair motor with DIP Switch S7 on
    if enable == True and rpm > 142:                  # rpm must be greater than 142 rpm
        Vout = (5*(rpm - 142))/(speedRange - 142)     # formulas for going from rpm to Vout are found in Motor Controller Instructions (5.1.4)
        print(Vout)
        GPIO.output(MEpin,GPIO.HIGH)                  # motor enabled
        if direction == 1:
            GPIO.output(MDpin,GPIO.LOW)               # motor clockwise turn
        elif direction == 2:
            GPIO.output(MDpin,GPIO.HIGH)              # motor counter-clockwise turn

        writeVoltage(Vout)                            # motor rpm set

    else:
        GPIO.output(MEpin,GPIO.LOW)                   # motor disable
	
def runCommand(motorRPM, directionVar, timeVar):
    print('Executing Command')
    setSolenoidValve(1) #GPIO.HIGH
    time.sleep(1)
    setMotor(True, directionVar, motorRPM)
    time.sleep(timeVar)
    setMotor(False, None, None) # Motor off
    setSolenoidValve(0) #GPIO.LOW
    time.sleep(2)

def changeBuoyancy(percent):
    #0 is 0 buoyancy, the robot will sink
    #1 is full buoyancy, the robot will rise

    currentBuoyancy = readBuoyancy()
    #I don't know if we will have fine enough control to get better than this
    if abs(percent - currentBuoyancy) > .3:
                if percent > currentBuoyancy:
                        #forward
                        GPIO.output(MDpin,GPIO.HIGH)
                else:
                        #backward
                        GPIO.output(MDpin,GPIO.LOW)
                #SValve = 1 open
                GPIO.output(SVpin,GPIO.HIGH)

                #MEnable = 1
                GPIO.output(MEpin,GPIO.HIGH)

                while abs(percent - currentBuoyancy) > .15:
                        currentBuoyancy = readBuoyancy()

                #MEnable = 0
                GPIO.output(MEpin,GPIO.LOW)
                #MDirection = 0
                GPIO.output(MDpin,GPIO.HIGH)
                #SValve = 0
                GPIO.output(SVpin,GPIO.HIGH)

def exit_cleanup():
        GPIO.cleanup(MEpin) # Motor Enable pin 17
        GPIO.cleanup(MDpin) # Motor Direction pin 18
        GPIO.cleanup(SVpin) # Solenoid Valve pin 22
        print("\n\nCleaning up pins\n\n")

def getStatusInfo():
    
    
    global serversocket
    
    msg = []
    
    serversocket.settimeout(5.0)
    
    # get local machine name
    host = (ip)
    port = 9000

    # bind to the port
    serversocket.bind((host, port))                                  

    # queue up to 5 requests
    serversocket.listen(4)

    msg.append("S")
    try:
        bus.read_byte(DAC_addr)
        msg.append("1")
    except:
        msg.append("0")

    try:
        bus.read_byte(ADC_addr)
        msg.append("1")
    except:
        msg.append("0")

    
    # establish a connection
    print( host)
    clientsocket = None
    #while(clientsocket == None):
    try:
            clientsocket,addr = serversocket.accept()
    except KeyboardInterrupt:
            exit_cleanup()
        
            #break
        #except:
          #  continue
    except socket.timeout as e:
        return
        
    with clientsocket:
        print("Got a connection from %s" % str(addr))

        msg.append("1")
        msg.append("1")
        message = ''.join(msg)
                
        clientsocket.send(message.encode('ascii'))
            
        clientsocket.close()
        


def collectData(pressure):
        global ptime
        global pdata
        if(time.clock() - ptime >= 1.0):
                ptime = time.clock()
                pdata.append((ptime,pressure))
        
def connect():
    global serversocket
    msg = []

    # queue up to 5 requests
    serversocket.listen(5)
    
    try:
        clientsocket,addr = serversocket.accept()
    except socket.timeout as e:
        return

    with clientsocket:
        print("Got a connection from %s" % str(addr))
       

        message = pickle.dumps([10,0,4,3,4,3,2,4,2,2,4,3,2,4])
        print(message)
        clientsocket.send(message)
        
        clientsocket.close()

def checkCommand():
    global serversocket

    serversocket.listen(5)
    
    try:
        clientsocket,addr = serversocket.accept()
    except socket.timeout as e:
        return

    with clientsocket:
        print("Received control command.")
        initialData = clientsocket.recv(1024)
        motorRPM, directionV, durationV = struct.unpack('iii', initialData)
        print("RPM: " + motorRPM + " Direction: " + directionV + " Duration: " + durationV)
        runCommand(motorRPM, directionV, durationV)
        clientsocket.close()

    #program starts
try:
    ADC_addr = 0x48
    DAC_addr = 0x60

    # Mapping of data/sample rate to config register values for ADS1015 (faster).
    programmable_gain_map = {6144: 0x0000, 4096: 0x0200, 2048: 0x0400, 1024: 0x0600, 512: 0x0800, 256: 0x0A00}
    channel_map = {0: 0x4000, 1: 0x5000, 2: 0x6000, 3: 0x7000} #map for channel
    samples_per_second_map = {128: 0x0000, 250: 0x0020, 490: 0x0040, 920: 0x0060, 1600: 0x0080, 2400: 0x00A0, 3300: 0x00C0} #sampling rate

    bus = SMBus(1)


    GPIO.setmode(GPIO.BCM) #sets pin numbering mode


    MEpin = 17 #off
    MDpin = 18 #forward
    SVpin = 22 #closed

    GPIO.setup(MEpin,GPIO.OUT,initial=GPIO.LOW) # Motor Enable pin MEpin
    GPIO.setup(MDpin,GPIO.OUT,initial=GPIO.LOW) # Motor Direction pin 18
    GPIO.setup(SVpin,GPIO.OUT,initial=GPIO.LOW) # Solenoid Valve pin 22

    #constants
    water_density = 1e3
    grav = 9.81

    ptime = time.clock()
    pdata = ["0"]

    maxPressure = .02 #Assuming PSI (~2m underwater)
    minPressure = .001

    ###################################
    ip = get('https://api.ipify.org').text
    print(ip)

    #status
    
    serversocket = socket.socket(socket.AF_INET, socket.SOCK_STREAM) 
    getStatusInfo()
    #except:
    #    print("DJFJ")

    #main loop
    while True:
            print("about to connect")
            #currentPressure = readPressure()
            collectData("12")
            connect()
            checkCommand()
            #if currentPressure > maxPressure:
                #changeBuoyancy(1) #Max Buoyancy

            #elif currentPressure < minPressure:
                #changeBuoyancy(0) #Min Buoyancy
except KeyboardInterrupt:
    exit_cleanup()

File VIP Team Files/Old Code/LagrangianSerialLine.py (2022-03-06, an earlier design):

# TODO: update to use correct method of toggling GPIO pins
#       add correct pins for i2c and update remaining code to use it for all analog signals
#
#  I2C over pins 2 and 3
#    12Bit ADC
#      Hall Effect Sensors 1 and 2
#      Pressure Sensor analog input
#    DAC
#      Motor Speed Analog Out


import RPi.GPIO as GPIO
from smbus2 import SMBus
import time
import socket
from requests import get
import pickle

def tabletopStartup(n):                # This fuction is only useful for the tabletop testing and has values hard coded
    rpm = 0
    for i in range(n):
        rpm += 500
        print("RPM = ", rpm)
        setSolenoidValve(GPIO.HIGH)
        time.sleep(2)
        setMotor(True, "CW", rpm)      # Motor running CW at multiples of 500 rpm up to n * 500 rpm
        time.sleep(5)
        setMotor(False, None, None)    # Turn off motor
        setSolenoidValve(GPIO.LOW)
        time.sleep(5)
        print("Reversing directions")
        setSolenoidValve(GPIO.HIGH)
        time.sleep(2)
        setMotor(True, "CCW", rpm)     # Motor running CCW at multiples of 500 rpm up to n * 500 rpm
        time.sleep(5)
        setMotor(False, None, None)    # Turn off motor
        setSolenoidValve(GPIO.LOW)
        time.sleep(5)   
        print("RPM = ", rpm, " finished") 
        
def customTest():
    mode = int(input("Press 1 for one direction, 2 for one direction and then reverse: "))
    runtime = int(input("Runtime: "))
    speed = int(input("RPM: "))
    direction = input("CW or CCW: ")

    if direction == "CW":
        reverse_dir = 'CCW'
    else:
        reverse_dir = 'CW'
    
    if mode == 1:
        setSolenoidValve(GPIO.HIGH)
        time.sleep(1)
        setMotor(True, direction, speed)      # Motor on
        time.sleep(runtime)                   # Motor runtime
        setMotor(False, None, None)           # Motor off
        setSolenoidValve(GPIO.LOW)
        time.sleep(2)
        print("Custom Test Complete!")
    else:
        setSolenoidValve(GPIO.HIGH)
        time.sleep(1)
        setMotor(True, direction, speed)      # Motor on
        time.sleep(runtime)                   # Motor runtime
        setMotor(False, None, None)           # Motor off
        setSolenoidValve(GPIO.LOW)
        time.sleep(2)
        print("Reversing direction")

        setSolenoidValve(GPIO.HIGH)
        time.sleep(1)
        setMotor(True, reverse_dir, speed)      # Motor on
        time.sleep(runtime)                   # Motor runtime
        setMotor(False, None, None)           # Motor off
        setSolenoidValve(GPIO.LOW)
        time.sleep(2)
        print("Custom Test Complete!")


def bleeding(sec):
    # Sends out air bubbles from the system by spinning in one direction continuously
    print("Starting bleeding in one direction")
    setSolenoidValve(GPIO.HIGH)
    time.sleep(1)
    setMotor(True, "CW", rpm=1000)      # Motor running CW at 1000 rpm
    time.sleep(sec)
    setMotor(False, None, None)        # Turn off motor
    setSolenoidValve(GPIO.LOW)
    time.sleep(2)
    print("Finished")
        
def writeVoltage(Vout):
    value  = int((4096*Vout)/5.0)
    if(value > 4095):
        value = 4095
    elif(value < 0): 
        value = 0 
    reg_data = [(value >> 4) & 0xFF, ((value & 0xF) << 4) & 0xFF]
    #reg_data = [int(value/16), (value % 16) << 4]
    
    bus.write_i2c_block_data(DAC_addr,0x60,reg_data)


def setMotor(enable, direction, rpm):                 
    speedRange = 11285                                # this if for a 7 pole pair motor with DIP Switch S7 on
    if enable == True and rpm > 142:                  # rpm must be greater than 142 rpm
        Vout = (5*(rpm - 142))/(speedRange - 142)     # formulas for going from rpm to Vout are found in Motor Controller Instructions (5.1.4)
        print(Vout)
        GPIO.output(MEpin,GPIO.HIGH)                  # motor enabled
        if direction == "CW":
            GPIO.output(MDpin,GPIO.LOW)               # motor clockwise turn
        else:
            GPIO.output(MDpin,GPIO.HIGH)              # motor counter-clockwise turn

        writeVoltage(Vout)                            # motor rpm set

    else:
        GPIO.output(MEpin,GPIO.LOW)                   # motor disable
    

def setSolenoidValve(val):
    # Retract if val == 0, extend if val == 1
    if (val == 1 or val == GPIO.HIGH):
        GPIO.output(SVpin, GPIO.HIGH)
    elif (val == 0 or val == GPIO.LOW):
        GPIO.output(SVpin, GPIO.LOW)

    
def exit_cleanup():
    GPIO.cleanup(MEpin) # Motor Enable pin 17
    GPIO.cleanup(MDpin) # Motor Direction pin 18
    GPIO.cleanup(SVpin) # Solenoid Valve pin 22
    print("\n\nCleaning up pins\n\n")

    
try:
    ADC_addr = 0x48
    DAC_addr = 0x60

    # Mapping of data/sample rate to config register values for ADS1015 (faster).
    programmable_gain_map = {6144: 0x0000, 4096: 0x0200, 2048: 0x0400, 1024: 0x0600, 512: 0x0800, 256: 0x0A00}
    channel_map = {0: 0x4000, 1: 0x5000, 2: 0x6000, 3: 0x7000} #map for channel
    samples_per_second_map = {128: 0x0000, 250: 0x0020, 490: 0x0040, 920: 0x0060, 1600: 0x0080, 2400: 0x00A0, 3300: 0x00C0} #sampling rate

    bus = SMBus(1)

    GPIO.setmode(GPIO.BCM) #sets pin numbering mode

    MEpin = 17 #off
    MDpin = 18 #forward
    SVpin = 22 #closed

    GPIO.setup(MEpin,GPIO.OUT,initial=GPIO.LOW) # Motor Enable pin 17
    GPIO.setup(MDpin,GPIO.OUT,initial=GPIO.LOW) # Motor Direction pin 18
    GPIO.setup(SVpin,GPIO.OUT,initial=GPIO.LOW) # Solenoid Valve pin 22

    # bleeding(25)
    # tabletopStartup(4)                 # n = 3, sample test loop number
    customTest() # placeholder till we get a decided sequence

except KeyboardInterrupt:
    #GPIO.output(MEpin,GPIO.LOW) # Disables motor on keyboard interrupt / don't have to call setMotor again
    #GPIO.output(MDpin,GPIO.LOW) # Motor Direction pin 18
    #GPIO.output(SVpin,GPIO.LOW) # Solenoid Valve pin 22
    #print("Did you just press C? Did you just kill me?")
    setMotor(False, None, None)
    print("setMotor executed")
    # exit_cleanup()
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

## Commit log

2022-03-06 Setting up the repository
    Merging files from the VIP Team's Lagrangian Profiler github (https://github.gatech.edu/Aquabots-VIP/LagrangianProfiler) into the RoboSharks repository.
    [105314-1108.stp, ControlBoard-B_Cu.gbr, ControlBoard-B_Mask.gbr, ControlBoard-B_Paste.gbr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]
2022-03-06 BMS Module PCB Gerber and BOM files
    Generated Gerber and BOM files for the BMS Module PCB.
    [aquabotsBMSModule-B_Cu.gbr, aquabotsBMSModule-B_Mask.gbr, aquabotsBMSModule-B_Paste.gbr, aquabotsBMSModule-B_Silkscreen.gbr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]
2022-03-07 BMS Controller Update
    Edited the board and created Gerber files.
    [aquabotsBMS-B_Cu.gbr, aquabotsBMS-B_Mask.gbr, aquabotsBMS-B_Paste.gbr, aquabotsBMS-B_Silkscreen.gbr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]
2022-03-10 Updated with new BMS Module PCB
    Fixed footprints on some of the components based on the replacements we selected when ordering parts. Nothing else was changed from the previous version except those footprints
    [aquabotsBMSModule mostly done but trying something.kicad_pcb, aquabotsBMSModule-B_Cu.gbr, aquabotsBMSModule-B_Fab.gbr, aquabotsBMSModule-B_Mask.gbr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]
2022-03-10 Deleted a previous unfinished version
    Deleted a previous version that was unfinished and was not the one we printed out. This will help to limit confusion for which PCB layout we chose
    [aquabotsBMSModule mostly done but trying something.kicad_pcb]
2022-03-11 Sensor Board File Update to Kicad 6
    Here we go
    [SensorBoard.kicad_pcb]
2022-03-14 MicroFloat Test Code Upload & BMS Controller PCB
    Copied RUR Arduino test code into our repository for easy access. Also created drill files and a new gerber ZIP for the BMS Controller PCB.
    [aquabotsBMS-B_Cu.gbr, aquabotsBMS-B_Mask.gbr, aquabotsBMS-B_Paste.gbr, aquabotsBMS-B_Silkscreen.gbr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]
2022-03-14 Control Board issues file added
2022-03-15 Updates to Kicad V6.0
    It updated from old format to the new format of Kicad
    [ControlBoard.kicad_pcb, ControlBoard.kicad_sch]
2022-03-15 First Control Board Update
    Added a cutout for the USB-C header.
    [ControlBoard-bottom-pos.csv, ControlBoard-top-pos.csv, ControlBoard.kicad_pcb, ControlBoard_BOM_20220315.csv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]
2022-03-20 Control Board Update #1
    Title
2022-03-22 Control Board Updates
    Made most of the changes suggested in "control board issues.txt", sent off an email to Matthew with some suggestions and questions. Will complete design and then start speccing parts after that.
    [ControlBoard.kicad_pcb, ControlBoard.kicad_sch]
2022-03-28 New Updates
    Created an I2C and SPI data bus. Routed all the corrections according to Matthew Woodward in the schematic. Still working on finishing the routing in the PCB editor.
    [ControlBoard.kicad_pcb, ControlBoard.kicad_sch]
2022-03-31 Update ControlBoard.kicad_pcb
    Latest changes to the routing for version 2
    [ControlBoard.kicad_pcb]
2022-04-01 Final Control Board Updates
    Finished the PCB routing and went through the DRC and corrected most errors.
    [ControlBoard.kicad_pcb, ControlBoard.kicad_sch]
2022-04-01 Update to Version 2
    Updated to add jumpers for the antenna switch on the LoRa. One is Vcc and the other is GND. Will need to test and solder once correct layout is found.
    [ControlBoard.kicad_pcb, ControlBoard.kicad_sch]
2022-04-13 Minor control board updates
    Lingering updates that hadn't been pushed, moved some silkscreen around, couple other miscellaneous updates.
    [ControlBoard-B_Cu.gbr, ControlBoard-B_Mask.gbr, ControlBoard-B_Paste.gbr, ControlBoard-B_Silkscreen.gbr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]
2022-04-13 Uploading Sensor Board Testing Code (Rough)
    Will need to be touched up later, this is just the first draft of all the Sensor Board testing code that was used today. Includes code for the MBED side as well as the Arduino side.
2022-04-27 New Matlab Simulations Folder
    Updated with my code for our Power Analysis and Antenna Simulations. Power is a rough estimation. I believe the current for the motor might be an overestimation but depends on the new control board.
2022-05-03 Adding CAD files from this semester
    CAD files from all of our current models and previous models we used are uploaded. Most are in internal files based on the subsystems.
    [4810T364_British Standard Low-Pressure Stainless Steel Pipe Fitting.SLDPRT, 90 degree Parker Hydraulics 2107-02-02.SLDPRT, ASCO - Solenoid - 8262H079.SLDPRT, A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]
2022-05-03 Prettyfied
    In a world where youre pretending to be a millionaire, Brooks Brothers won't cut it.

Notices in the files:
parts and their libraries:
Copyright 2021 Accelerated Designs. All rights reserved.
